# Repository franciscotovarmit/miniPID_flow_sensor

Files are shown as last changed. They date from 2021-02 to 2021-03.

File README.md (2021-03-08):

# miniPID flow sensor

This device measures the flow rate of the [Aurora Scientific 200B miniPID](https://aurorascientific.com/products/legacy-applications/environmental-monitoring/minipid-dispersion-sensor/) photo-ionization detector. At its heart lies a Renesas FS2012-1020-NG calibrated mass flow sensor, which is rated for 0 to 2 SLPM. [Will Dickson](https://github.com/willdickson) wrote the [original firmware and software](https://github.com/willdickson/fs2012_flow_sensor), which I [slightly modified](https://github.com/hanhanhan-kim/fs2012_flow_sensor) to make Python 3-compatible.

## Hardware

### BOM

In addition to standard electronics equipment and access to a 3D-printer:

| Item                       | Price (USD)    | Quantity | Source                                                       |
| -------------------------- | -------------- | -------- | ------------------------------------------------------------ |
| FS2012-1020-NG             | 94.90          | 1        | DigiKey <br />[800-3797-ND](https://www.digikey.com/en/products/detail/renesas-electronics-america-inc/FS2012-1020-NG/7645225?s=N4IgjCBcoLQBxVAYygMwIYBsDOBTANCAPZQDaIcADJSALoC%2B9hATGSAGIDKzlYzMYSjxgA5AOJ16QA) |
| Arduino Nano (clone)       | 13.99 / 3      | 1        | Amazon <br />ASIN: [B0713XK923](https://www.amazon.com/ELEGOO-Arduino-ATmega328P-Without-Compatible/dp/B0713XK923/ref=sr_1_2_sspa?dchild=1&keywords=arduino+nano+clone&qid=1614064204&sr=8-2-spons&psc=1&spLa=ZW5jcnlwdGVkUXVhbGlmaWVyPUEzUDZEOUk0VThIM1BIJmVuY3J5cHRlZElkPUEwMTUxMDMwMkhZV1dXNVdQRk43OCZlbmNyeXB0ZWRBZElkPUEwNjcwMjY5M0tNOEVIT0dVR1BLSiZ3aWRnZXROYW1lPXNwX2F0ZiZhY3Rpb249Y2xpY2tSZWRpcmVjdCZkb05vdExvZ0NsaWNrPXRydWU=) |
| Silicone tubing (3/16" ID) | 7.99 / 10 feet | 1        | Amazon <br />ASIN: [B07TH8H1QP](https://www.amazon.com/gp/product/B07TH8H1QP/ref=ppx_yo_dt_b_asin_title_o02_s00?ie=UTF8&th=1) |

The sensor can be swapped out for an alternative Renesas FS2012-series sensor, such as the [FS2012-1100-NG](https://www.digikey.com/en/products/detail/renesas-electronics-america-inc/FS2012-1100-NG/7645220?s=N4IgjCBcoLQBxVAYygMwIYBsDOBTANCAPZQDaIcADJSALoC%2B9hATGSAGIDKzlYzMYMNRgA5AOJ16QA), which is rated for 0 to 10 SLPM. 

The adaptor between the FS2012 sensor and the long metal PID inlet is 3D-printed. The measured OD of the PID's metal inlet is approximately **1.30 mm**. In my experience, printing an exact 1.30 mm ID hole on an FDM printer is tricky, and requires some trial and error. I provide a [`.gcode` file](CAD_files/PID_flow_sensor_for_prusa_mk3s_0.2mm_PLA_MK3S_9m.gcode) that worked for me on a Prusa MK3S with Prusament PLA. Adjustments can be made with the provided [`.step` file](CAD_files/PID_flow_sensor_for_prusa_mk3s.step). A corresponding [`.stl` file](CAD_files/PID_flow_sensor_for_prusa_mk3s.stl) is also provided. *N.B.* I've tried generating `.stl` and `.gcode` files for printing the adaptor with TPU, but I've not yet had any luck.

### Hook-up

| Arduino Nano pin                             | FS2012 sensor pin |
| -------------------------------------------- | ----------------- |
| 5 V                                          | VIN               |
| GND                                          | GND               |
| A5 or A6 (can be modified in `firmware.ino`) | VOUT              |

The firmware supports up to two flow sensors, for which GND and VIN are common. 

### Assembly

Use the silicone tubing to secure the components together. The assembled sensor, prior to electrical hook-up, might look something like this:

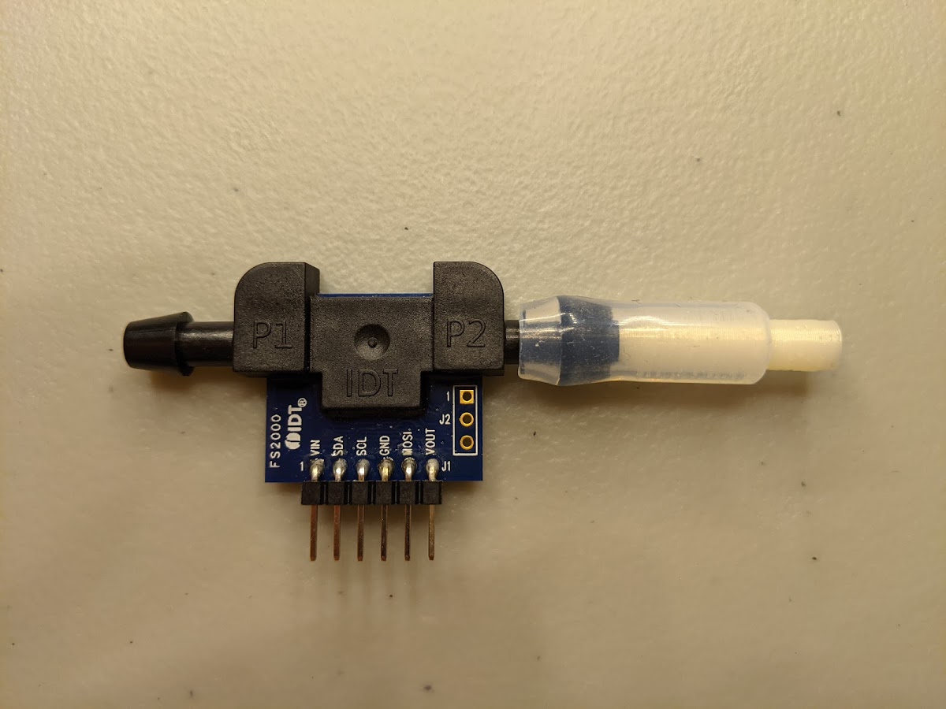
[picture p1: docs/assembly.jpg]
Pre-hook-up assembly


If you're having difficulty adjusting your printer settings so that the adaptor press-fits against the PID inlet, or you're in a rush, just bodge it with some parafilm. Parafilm might not be a bad idea, even if the adaptor fits snugly. The assembled flow sensor device might look something like this:

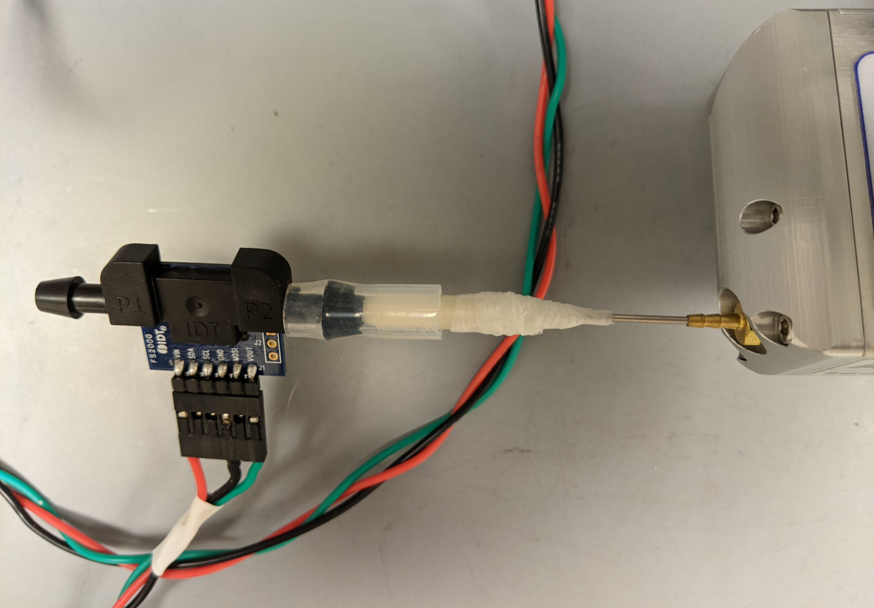
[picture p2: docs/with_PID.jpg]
Assembled


### Additional notes

Clean the inside of the 3D-printed adaptor prior to use. I recommend going through the channel with some kind of filament (e.g. some solder) to clear away large particulate debris. Then, apply some air pressure through the channel to rid of any remaining particulates. 

## Data collection

Collecting data with the device is straightforward. Clone the [FS2012 flow sensor repo](https://github.com/hanhanhan-kim/fs2012_flow_sensor), upload the firmware, and install the software. The software is Python 3-compatible only. For a Python 2-compatible version of the code, see the [original repo](https://github.com/willdickson/fs2012_flow_sensor). Then, call the relevant Python function (probably `DataReader(<my_port>).get_data()`) in your acquisition script. Alternatively, for something quick, try out the existing `flow_sensor_app` or `flow_sensor_live_plot` scripts:

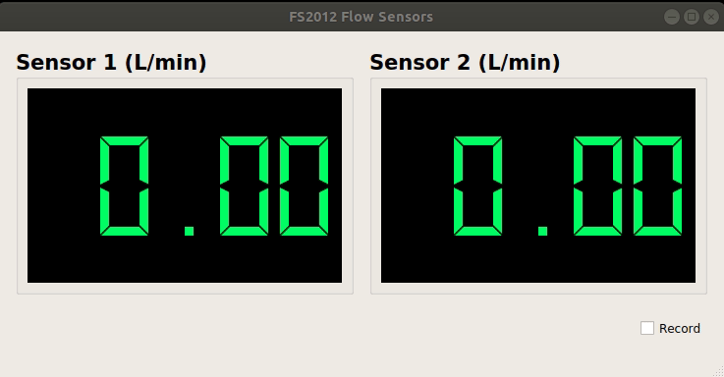
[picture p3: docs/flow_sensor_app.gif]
app_demo


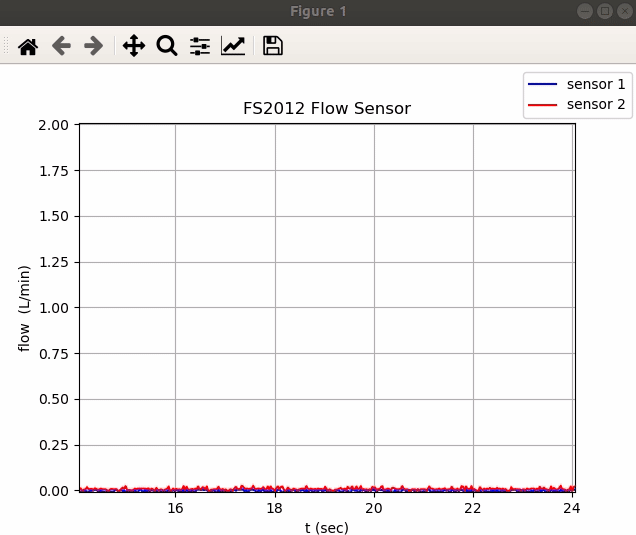
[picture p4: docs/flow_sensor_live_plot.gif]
live_plot_demo


See the [FS2012 flow sensor repo](https://github.com/hanhanhan-kim/fs2012_flow_sensor) for more details.

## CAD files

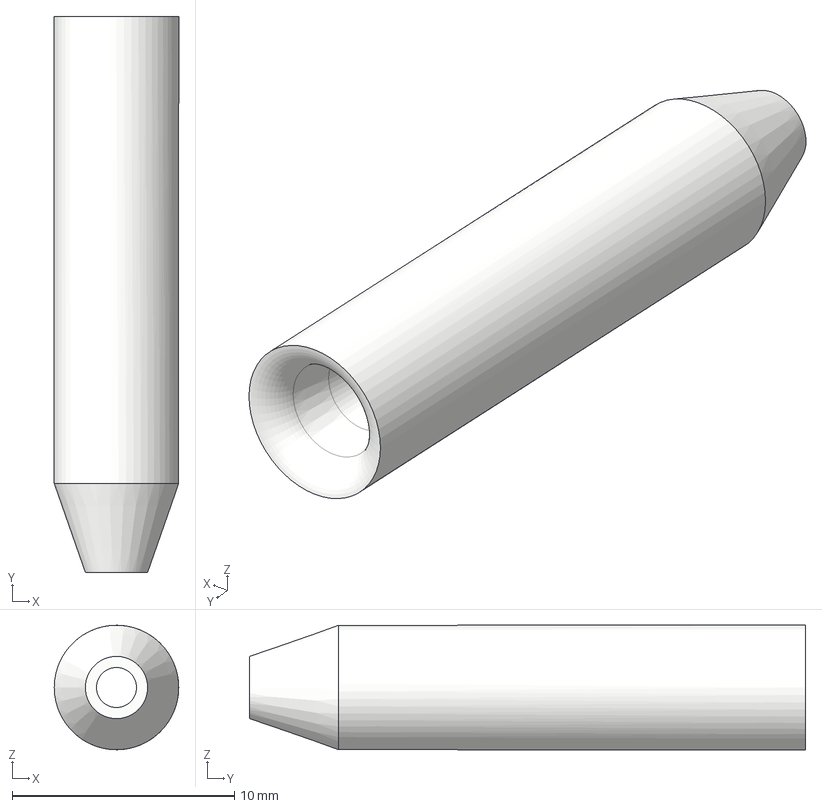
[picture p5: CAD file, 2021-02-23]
CAD_files/PID_flow_sensor_for_prusa_mk3s.step
5.60 x 25.0 x 5.60 mm

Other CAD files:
CAD_files/PID_flow_sensor_for_prusa_mk3s.stl

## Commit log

2021-02-23 init repo
    [PID_flow_sensor_for_prusa_mk3s.step, PID_flow_sensor_for_prusa_mk3s.stl, PID_flow_sensor_for_serviced_PA11.stl]
2021-02-27 add assembly photo, gifs, and note about parafilm
2021-03-08 rm design for sending to service
    [PID_flow_sensor_for_serviced_PA11.stl]
